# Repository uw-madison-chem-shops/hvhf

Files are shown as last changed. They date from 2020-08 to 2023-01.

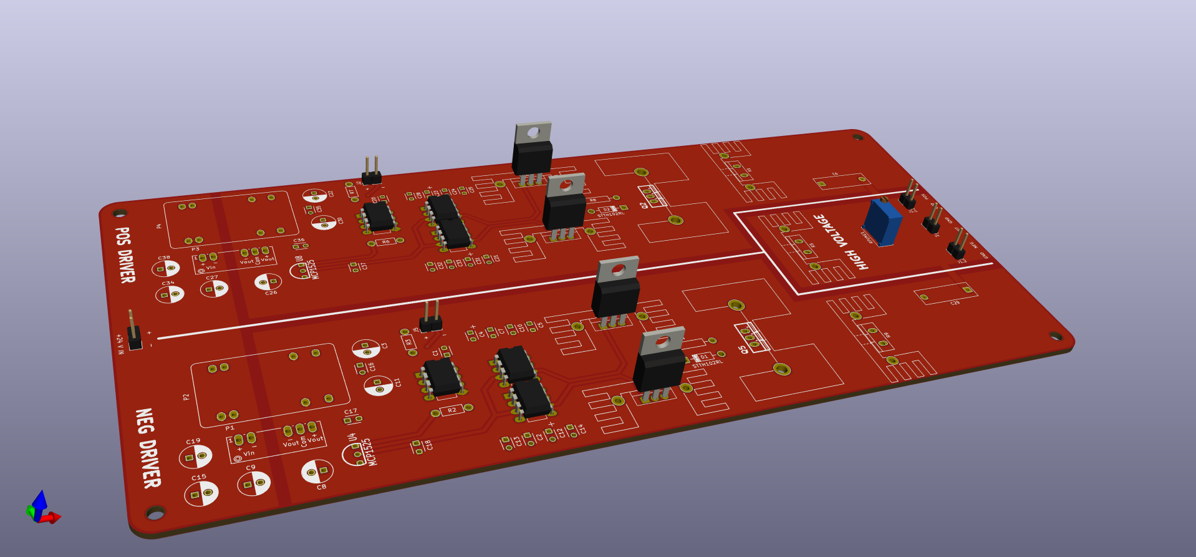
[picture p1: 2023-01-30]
kicad/HV-pulse-generator.png

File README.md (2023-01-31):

# High Voltage High Frequency

Adapted from "Note: An inexpensive square waveform ion funnel driver". https://doi.org/10.1063/1.4974345

## PCB

This PCB was designed using KiCAD version 5.
Refer to `HV-pulse-genrator.pdf` for schematic.
PCB images generated with [tracespace](https://github.com/tracespace/tracespace) follow.




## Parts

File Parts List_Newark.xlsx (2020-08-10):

HVHF Pulser
PER BOARD
Label | Value | Digikey | Newark | Quantity | Inventory
C1,C13,C18,C31 | 2.2uF Tantalum 35V | 478-1871-ND | 81H0636 | 4 | 0
C2,C8,C12,C16,C17,C19,C24,C28,C30,C34 | 100uF Electrolytic 35V | 732-9215-1-ND | 75Y5944 | 10 | 0
C3,C7,C9,C14,C20,C23,C25,C32 | 0.01uF Ceramic 50V | 399-9712-ND | 33C9028 | 8 | 1
C4,C15,C21,C33 | 1uF Ceramic 50V | 445-173257-1-ND | 96Y7421 | 4 | 1
C5,C10,C22,C26 | 0.1uF Cermaic 50V | 478-6008-ND | 95W2707 | 4 | 0
C6,C29 | 0.22uF Film 630V | PCF1578-ND | 49W2497 | 2 | 4
C11,C27 | 10uF 50V | 490-14508-ND |  | 2 | 3
D1,D2 | STTH102RL Diode 200V 1A | 497-6590-1-ND |  | 2 | 11
J1 | Molex Header, 3 pin | WM6393-ND | 34R5563 | 1 | 0
 | Molex pin contacts |  | 54H4931 | 5 | 0
J2,J3,J5 | Header, 2 pin |  | 56H2245 | 1 | 1 | Use 36 pin and cut off what you need
 | Crimp Contact |  | 46P5397 | 1 | 0 | Order 100 and use as needed
J4 | Molex Header, 2 pin | WM9127-ND | 34R5562 | 1 | 0
P1,P3 | PEM2-S24-S5-S 5V 2W DC/DC | 102-2784-ND |  | 2 | 0
P2,P4 | JCJ0824D15 8W +/- 15V DC/DC | 1470-1977-5-ND |  | 2 | 2
Q1,Q4 | VP0104 PMOSFET 40V 0.25A | VP0104N3-G-ND | 55AC4285 | 2 | 9
Q2 | FQP3P50 PMOSFET 500V 2.7A | FQP3P50-ND |  | 1 | 1
Q3,Q6 | VN0104 NMOSFET 40V 0.35A | VN0104N3-G-ND | 55AC4279 | 2 | 7
Q5 | FQP13N50 NMOSFET 500V 12.5A | FQP13N50-ND | 97K0164 | 1 | 1
R1,R9 | 50 Ohm 50W | MP850-50.0-F-ND | 63J8560 | 2 | 0
R2,R3,R6,R7 | 365 Ohm 0.6W | PPC365ZCT-ND | 97K5769 | 4 | 0
R4,R8 | 5.1 Ohm 3W | P5.1W-3BK-ND | 23AC4934 | 2 | 4
R5 | 100 Ohm 50W | 696-1329-ND | 40Y2762 | 1 | 5
U1,U4,U5,U8 | LM7171 200MHz VFB Op-Amp | LM7171BIN/NOPB-ND | 41K6277 | 4 | 10
U2,U6 | ICPL2631 2CH Optoisolator | ICPL2631-ND |  | 2 | 0
U3,U7 | MCP1525 2.5V Vreference | MCP1525-I/TO-ND | 89C7117 | 2 | 5
H1,H2 | Heatsink TO-220 4 C/W | RA-T2X-38E-ND | 92R5228 | 2 | 1
H3 | Heatsink TO-220 8 C/W | AE10799-ND |  | 1 | 1
H4,H5 | Heatsink TO-220 10 C/W | AE10807-ND |  | 2 | 1
P0 | PSU 24V 3.2A | 285-1827-ND | 08N3010 | 1 | 0
 | BNC Chassis |  | 92B6175 | 1 | 17
 | BNC Cable |  | 93F1398 | 2 | 26
 | SHV Chassis |  | 46F6040 | 3 | 8
 | SHV Cable |  | 46F6039 | 6 | 34
 | Cooling fan |  | 96M8211 | 1 | 1
 | Mounting screws 4-40 |  | Grainger | 8 | 999
 | Fuse Holder |  | 03420014H | 1 | 0
 | Fuse |  | 25R5371 | 2 | 0
 | Power Switch |  | 94T9282 | 1 | 0
 | Box |  | ET3/35B | 1 | 3 | Use 300mm boxes up first
 | Power Entry |  | 17B6838 | 1 | 0

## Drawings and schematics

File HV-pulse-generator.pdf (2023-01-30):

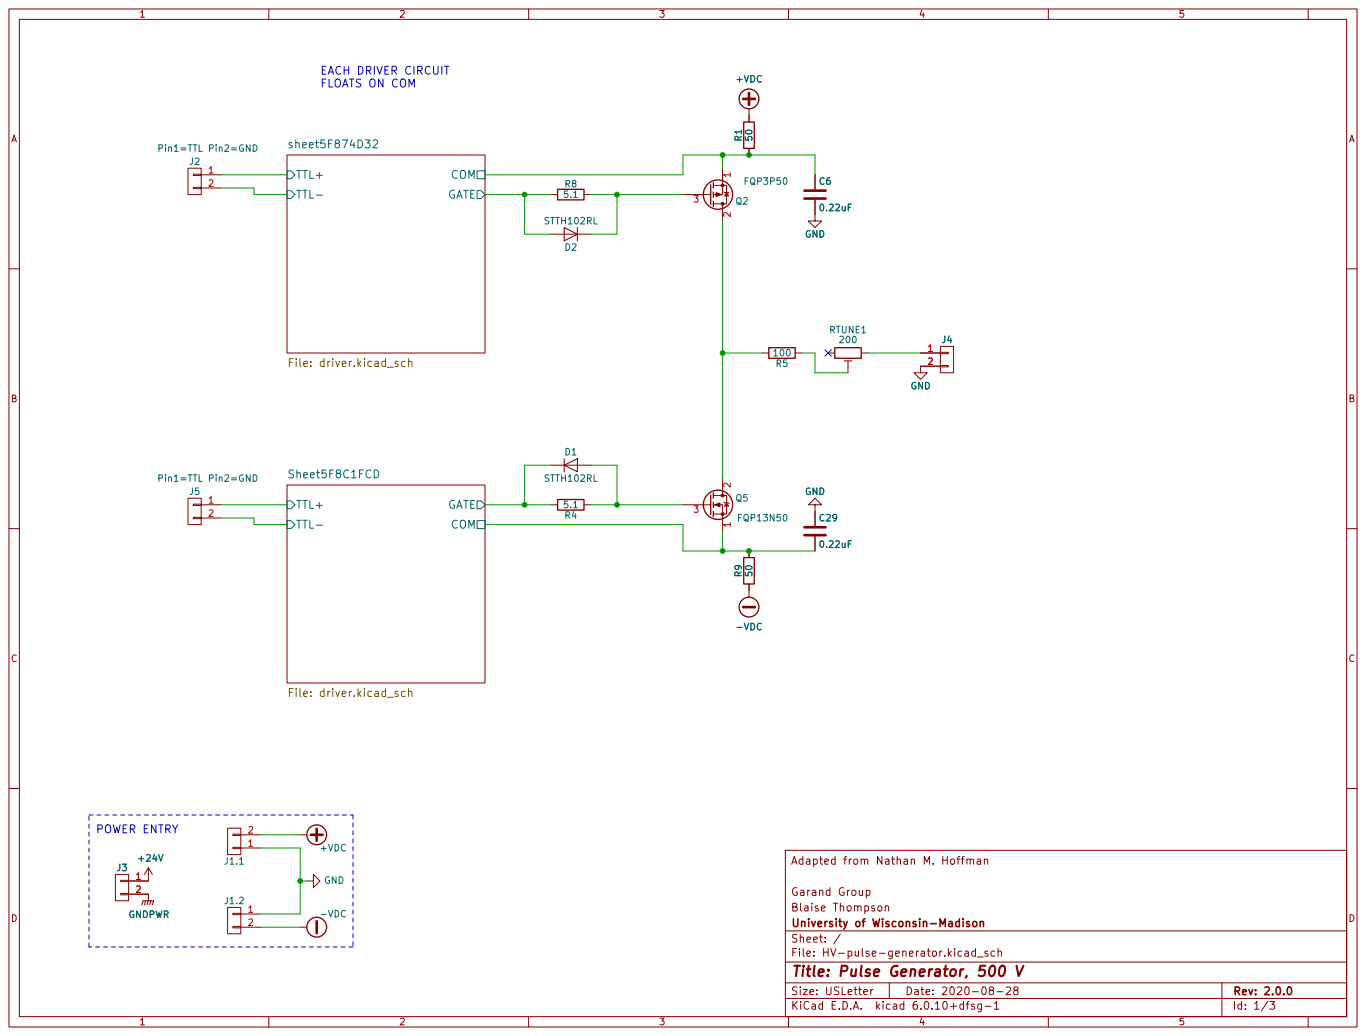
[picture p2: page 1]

Adapted from Nathan M. Hoffman

Garand Group
Blaise Thompson
File: HV-pulse-generator.kicad_sch Sheet: / University of Wisconsin-Madison

Id: 1/3 Title: Pulse Generator, 500 V

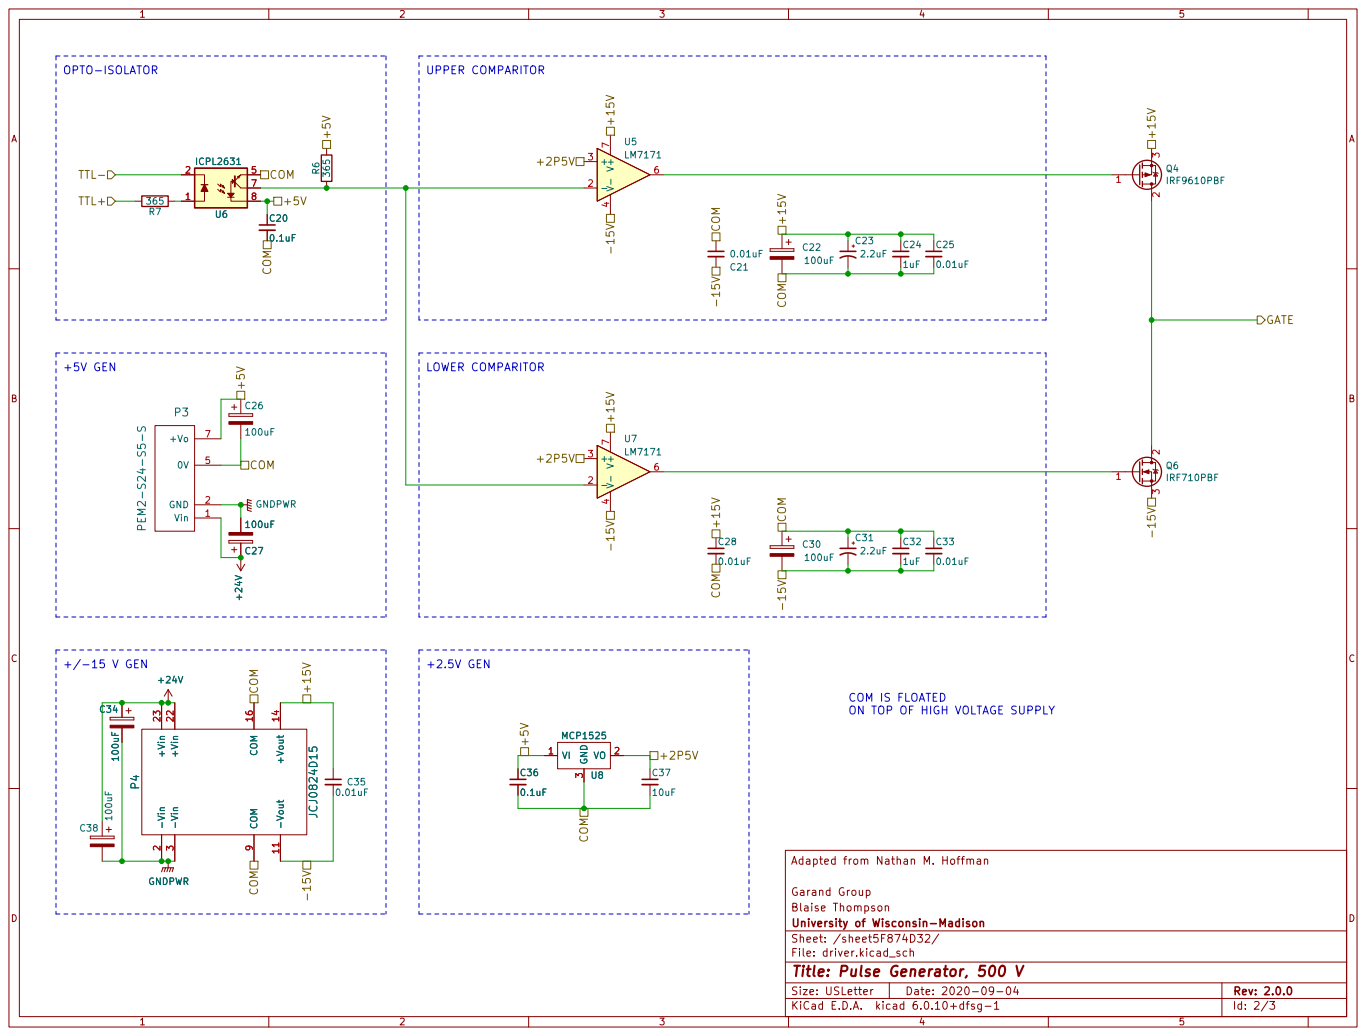
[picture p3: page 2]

COM IS FLOATED
ON TOP OF HIGH VOLTAGE SUPPLY

0.01uF -Vout 11 +Vout 14 COM 16 -Vin

Adapted from Nathan M. Hoffman GNDPWR

Garand Group
Blaise Thompson
File: driver.kicad_sch Sheet: /sheet5F874D32/ University of Wisconsin-Madison

Id: 2/3 Title: Pulse Generator, 500 V

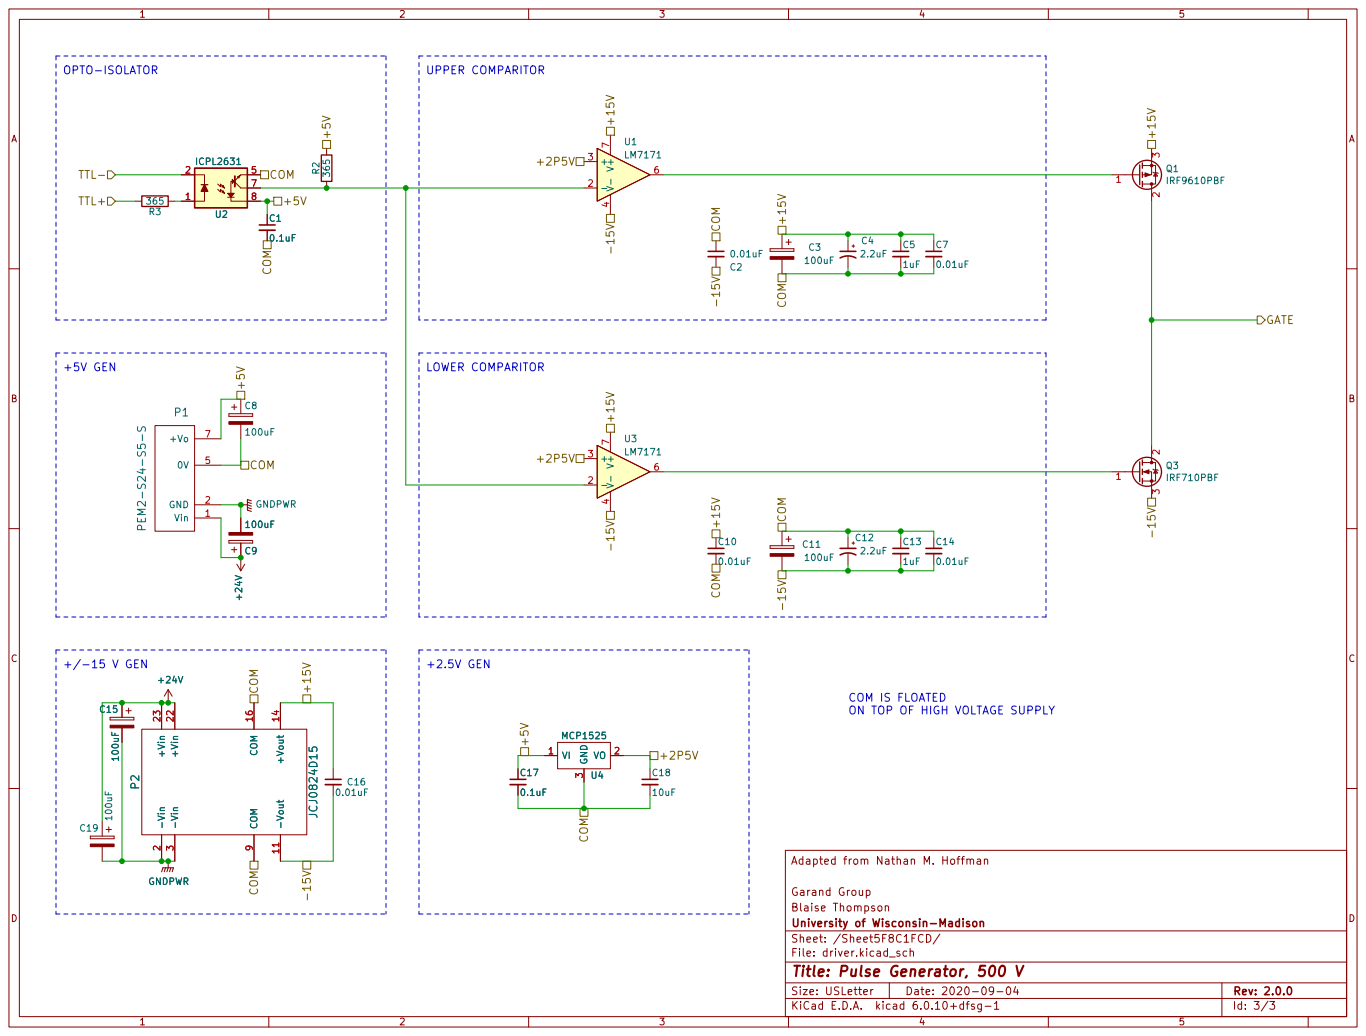
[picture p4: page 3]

COM IS FLOATED
ON TOP OF HIGH VOLTAGE SUPPLY

Garand Group
Blaise Thompson
File: driver.kicad_sch Sheet: /Sheet5F8C1FCD/ University of Wisconsin-Madison

Id: 3/3 Title: Pulse Generator, 500 V

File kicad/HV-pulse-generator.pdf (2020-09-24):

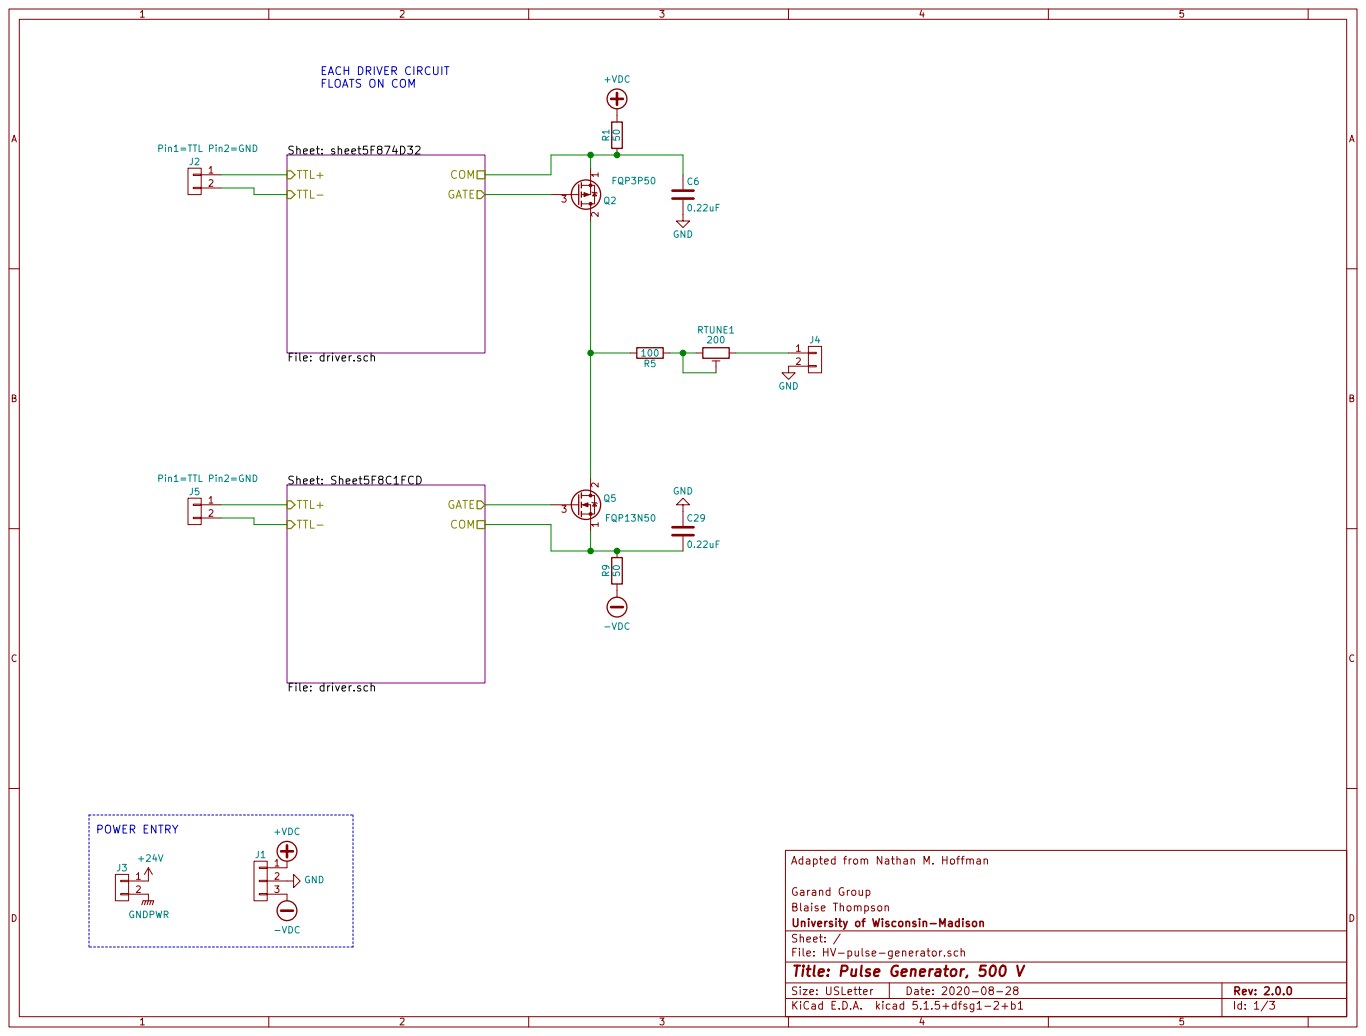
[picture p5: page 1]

J4 GND EACH DRIVER CIRCUIT
FLOATS ON COM

Adapted from Nathan M. Hoffman

Garand Group
Blaise Thompson
File: HV-pulse-generator.sch Sheet: / University of Wisconsin-Madison

Id: 1/3 Title: Pulse Generator, 500 V

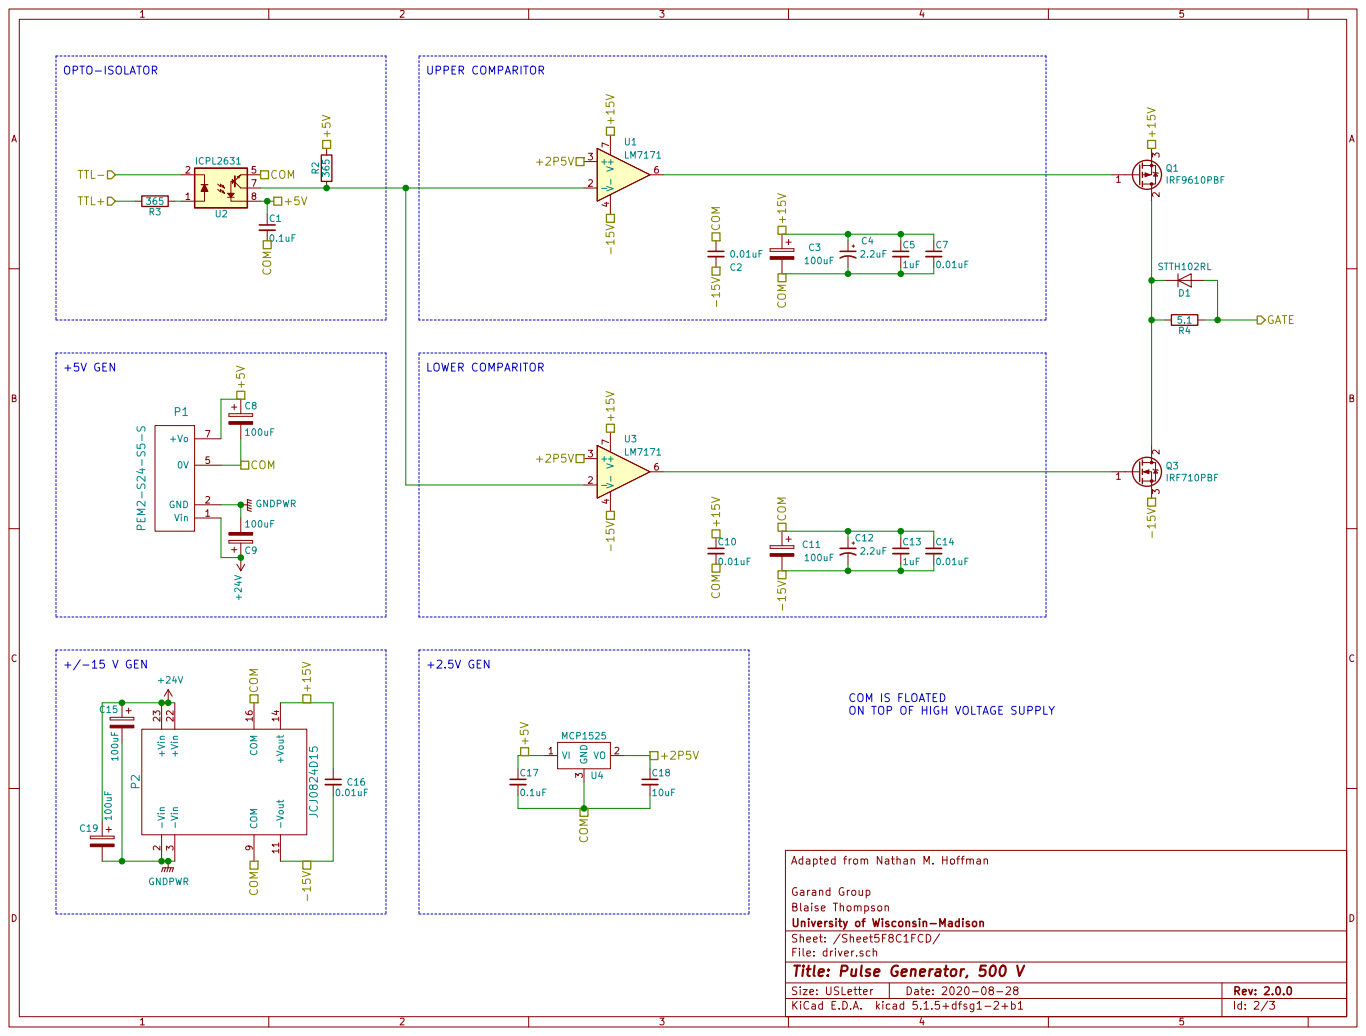
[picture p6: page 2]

COM IS FLOATED
ON TOP OF HIGH VOLTAGE SUPPLY

Adapted from Nathan M. Hoffman

Garand Group
Blaise Thompson
File: driver.sch Sheet: /Sheet5F8C1FCD/ University of Wisconsin-Madison

Id: 2/3 Title: Pulse Generator, 500 V

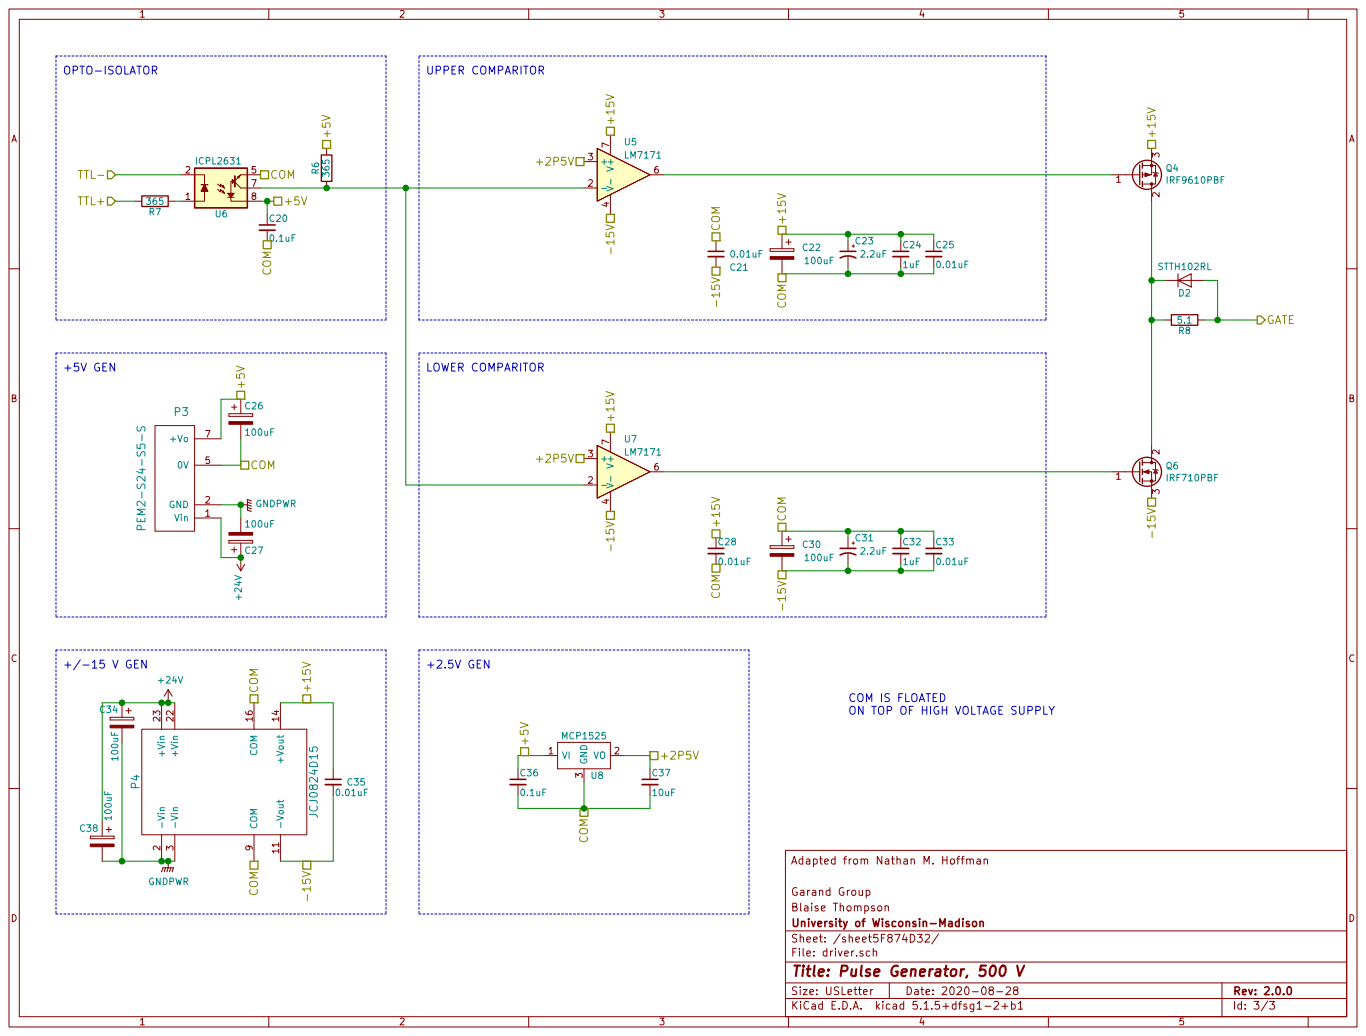
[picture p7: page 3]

COM IS FLOATED
ON TOP OF HIGH VOLTAGE SUPPLY

Adapted from Nathan M. Hoffman

Garand Group
Blaise Thompson
File: driver.sch Sheet: /sheet5F874D32/ University of Wisconsin-Madison

Id: 3/3 Title: Pulse Generator, 500 V

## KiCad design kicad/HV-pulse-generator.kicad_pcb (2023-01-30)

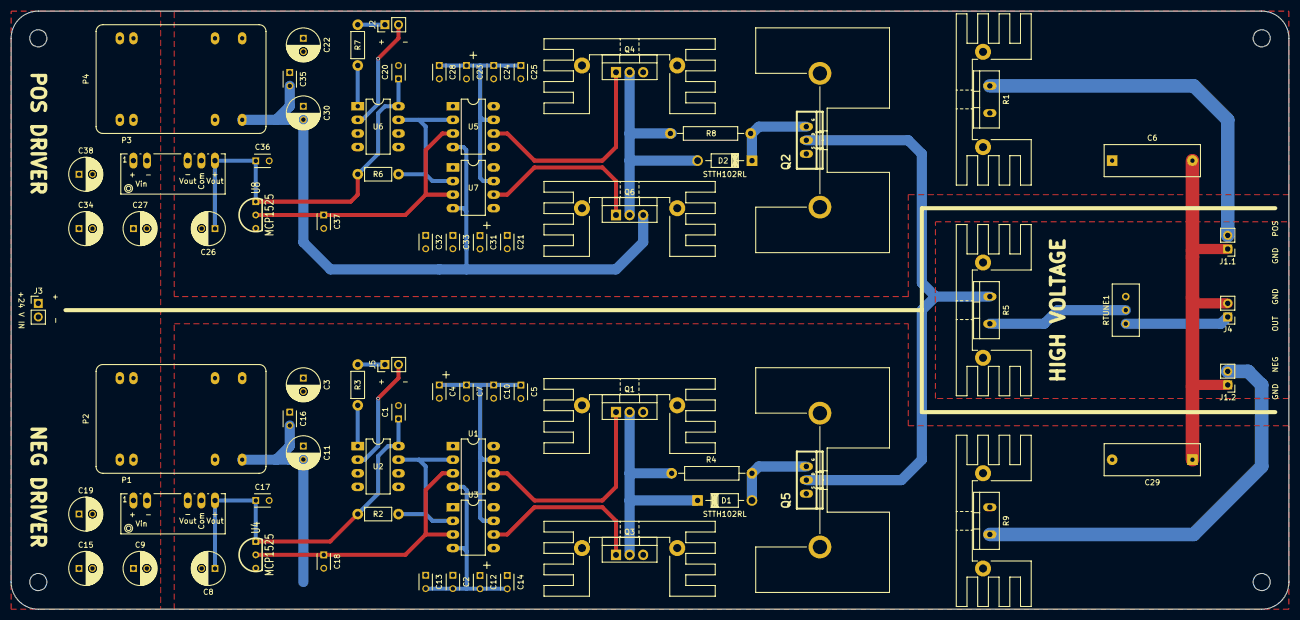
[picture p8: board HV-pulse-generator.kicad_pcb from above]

Board: 2 copper layers, 238.8 x 111.8 mm, 74 parts (0 on the bottom side), 34 nets.

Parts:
C1, C17, C20, C36: 0.1uF; C_Disc_D3_P2.5
C2, C7, C10, C14, C16, C21, C25, C28, C33, C35: 0.01uF; C_Disc_D3_P2.5
C3, C8, C9, C11, C15, C19, C22, C26, C27, C30, C34, C38: 100uF; C_Radial_D6.3_L11.2_P2.5
C4, C12, C23, C31: 2.2uF; C_Tantalum_D3_P2.5
C5, C13, C24, C32: 1uF; C_Disc_D3_P2.5
C6, C29: 0.22uF; ECW-FA2J(10-68)4J
C18, C37: 10uF; C_Disc_D3_P2.5
D1, D2: STTH102RL; Diode_DO-41_SOD81_Horizontal_RM10
J1.1, J1.2, J3: Pin1=24V Pin2=GND; PinHeader_1x02_P2.54mm_Vertical
J2, J5: Pin1=TTL Pin2=GND; PinHeader_1x02_P2.54mm_Vertical
J4: CONN_01X02; PinHeader_1x02_P2.54mm_Vertical
P1, P3: PEM2-S24-S5-S; DCDC-Conv_CUI_PEM2_DUAL
P2, P4: JCJ0824D15
Q1, Q4: IRF9610PBF; TO-220-3_Vertical
Q2: FQP3P50; FQP3P20
Q3, Q6: IRF710PBF; TO-220-3_Vertical
Q5: FQP13N50; FQP4N20L
R1, R9: 50; Resistor_TO-220_Vertical
R2, R3, R6, R7: 365; Resistor_Horizontal_RM7mm
R4, R8: 5.1; Resistor_Horizontal_RM15mm
R5: 100; Resistor_TO-220_Vertical
RTUNE1: 200; Potentiometer_Bourns_3296W_Vertical
U1, U3, U5, U7: LM7171; DIP-8_W7.62mm_LongPads
U2, U6: ICPL2631; DIP-8_W7.62mm_LongPads
U4, U8: MCP1525; TO92-MCP1525

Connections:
+24V: C9.1, C15.1, C19.1, C27.1, C34.1, C38.1, J3.1, P1.1, P2.22, P2.23, P3.1, P4.22, P4.23
+VDC: J1.1.2, R1.2
-VDC: J1.2.2, R9.1
/Sheet5F8C1FCD/+2P5V: C18.1, U1.3, U3.3, U4.2
/Sheet5F8C1FCD/+5V: C1.1, C8.1, C17.1, P1.7, R2.2, U2.8, U4.1
/Sheet5F8C1FCD/+15V: C3.1, C4.1, C5.1, C7.1, C10.1, C16.1, P2.14, Q1.3, U1.7, U3.7
/Sheet5F8C1FCD/-15V: C2.2, C11.2, C12.2, C13.2, C14.2, C16.2, P2.11, Q3.3, U1.4, U3.4
/Sheet5F8C1FCD/COM: C1.2, C2.1, C3.2, C4.2, C5.2, C7.2, C8.2, C10.2, C11.1, C12.1, C13.1, C14.1, C17.2, C18.2, C29.2, P1.5, P2.9, P2.16, Q5.1, R9.2, U2.5, U4.3
/Sheet5F8C1FCD/GATE: D1.1, Q1.2, Q3.2, R4.2
/Sheet5F8C1FCD/TTL+: J5.1, R3.2
/Sheet5F8C1FCD/TTL-: J5.2, U2.2
/sheet5F874D32/+2P5V: C37.1, U5.3, U7.3, U8.2
/sheet5F874D32/+5V: C20.1, C26.1, C36.1, P3.7, R6.2, U6.8, U8.1
/sheet5F874D32/+15V: C22.1, C23.1, C24.1, C25.1, C28.1, C35.1, P4.14, Q4.3, U5.7, U7.7
/sheet5F874D32/-15V: C21.2, C30.2, C31.2, C32.2, C33.2, C35.2, P4.11, Q6.3, U5.4, U7.4
/sheet5F874D32/COM: C6.1, C20.2, C21.1, C22.2, C23.2, C24.2, C25.2, C26.2, C28.2, C30.1, C31.1, C32.1, C33.1, C36.2, C37.2, P3.5, P4.9, P4.16, Q2.1, R1.1, U6.5, U8.3
/sheet5F874D32/GATE: D2.2, Q4.2, Q6.2, R8.1
/sheet5F874D32/TTL+: J2.1, R7.2
/sheet5F874D32/TTL-: J2.2, U6.2
GND: C6.2, C29.1, J1.1.1, J1.2.1, J4.2
GNDPWR: C9.2, C15.2, C19.2, C27.2, C34.2, C38.2, J3.2, P1.2, P2.2, P2.3, P3.2, P4.2, P4.3
unnamed: D1.2, Q5.3, R4.1
unnamed: D2.1, Q2.3, R8.2
unnamed: J4.1, RTUNE1.3
unnamed: Q1.1, U1.6
unnamed: Q2.2, Q5.2, R5.2
unnamed: Q3.1, U3.6
unnamed: Q4.1, U5.6
unnamed: Q6.1, U7.6
unnamed: R2.1, U1.2, U2.7, U3.2
unnamed: R3.1, U2.1
unnamed: R5.1, RTUNE1.2
unnamed: R6.1, U5.2, U6.7, U7.2
unnamed: R7.1, U6.1
